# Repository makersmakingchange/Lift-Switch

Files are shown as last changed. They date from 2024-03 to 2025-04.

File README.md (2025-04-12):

<!---  Open Source Assistive Technology: GitHub Readme Template Version 1.1 (2024-Mar-15)  --->

<!-- TITLE --->
# Lift Switch
<!--- SUMMARY -->
<!-- A brief summary of the project. What it does, who it is for, how much it costs. -->
The Lift Switch is a device that modifies the output from your assistive switch. The primary case is for a user who would prefer to rest on their switch and lift off of it to activate it, instead of requiring the user to hover over the switch. There are four operating modes: momentary, latching, timed latch, and reverse acting, described below:
- Momentary: The output will turn on momentarily when you lift off of the assistive switch.
- Latching: The output toggles between on/off when you lift off of the assistive switch.
- Timed Latch: The output will turn on for a set amount of time (7s) when you lift off of the assistive switch.
- Reverse Acting: Reverses the action of an assistive switch. Assistive switch off (not activated) = Lift Switch on, Assistive switch on (activated) = Lift Switch off.

The Lift Switch can also be used as a mouse click in any of the above modes, by plugging the Lift Switch into a computer through a USB cable.

The total cost of materials to build this device is around \$75 (plus component shipping). The cost of materials per unit is around \$43 (plus component shipping) if you are able to build in bulk.

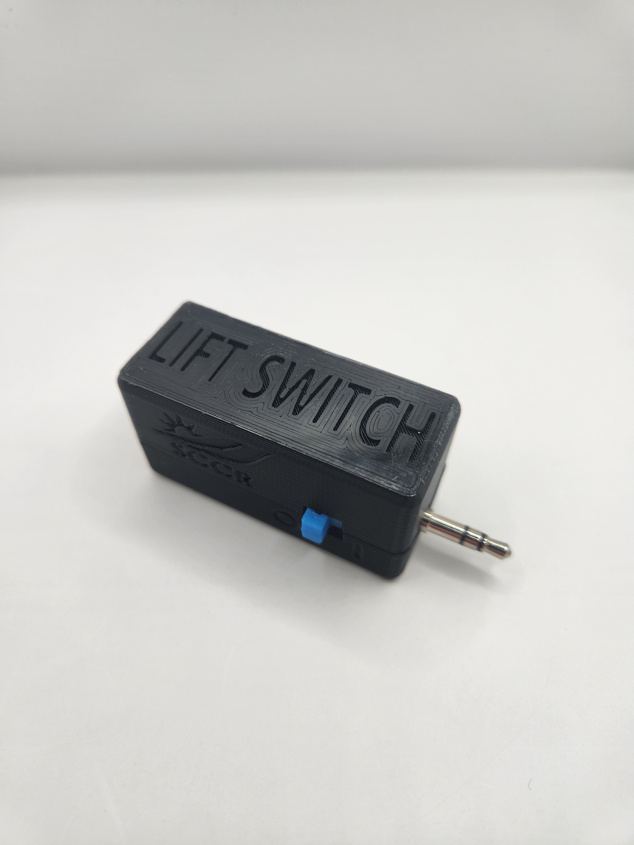
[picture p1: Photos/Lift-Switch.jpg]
Picture of the Lift Switch.


## Makers Making Change Assistive Device Library Listing
- https://www.makersmakingchange.com/s/product/lift-switch/01tJR000003UiczYAC

## How to Obtain the Device
### 1. Do-it-Yourself (DIY) or Do-it-Together (DIT)

This is an open-source assistive technology, so anyone is free to build it. All of the files and instructions required to build the device are contained within this repository. Refer to the Maker Guide below.

### 2. Request a build of this device

You may also submit a build request through the [Makers Making Change Assistive Device Library Listing](https://www.makersmakingchange.com/s/product/lift-switch/01tJR000003UiczYAC) to have a volunteer maker build the device. As the requestor, you are responsible for reimbursing the maker for the cost of materials and any shipping.

### 3. Build this device for someone else

If you have the skills and equipment to build this device, and would like to donate your time to create the device for someone who needs it, visit the [MMC Maker Wanted](https://makersmakingchange.com/maker-wanted/) section.

## Build Instructions

### 1. Read through the Maker Guide

The [Maker Guide](/Documentation/Lift_Switch_Maker_Guide.pdf) contains all the necessary information to build this device, including tool lists, assembly instructions, programming instructions and testing.

### 2. Order the Off-The-Shelf Components

The [Bill of Materials](/Documentation/Lift_Switch_BOM.csv) lists all of the parts and components required to build the device.

### 3. Order the Custom PCB

This device requires a custom PCB. Instructions are provided in the [Maker Guide](/Documentation/Lift_Switch_Maker_Guide.pdf) and the PCB fabrication files are available in the [PCB Build Files](/Build_Files/PCB_Build_Files).

### 4. Print the 3D Printable components

All of the files and individual print files can be in the [/Build_Files/3D_Printing_Files](/Build_Files/3D_Printing_Files/) folder.

### 5. Assemble the Lift Switch

Reference the [Maker Guide](/Documentation/Lift_Switch_Maker_Guide.pdf) for the tools and steps required to build each portion.

## How to improve this Device
As open source assistive technology, you are welcomed and encouraged to improve upon the design. 

## Files
### Documentation
| Document             | Version | Link |
|----------------------|---------|------|
| Maker Guide          | 1.0     | [Lift_Switch_Maker_Guide](/Documentation/Lift_Switch_Maker_Guide.pdf)     |
| Bill of Materials    | 1.0     | [Lift_Switch_Bill_of_Materials](/Documentation/Lift_Switch_BOM.csv)     |
| User Guide           | 1.0     | [Lift_Switch_User_Guide](/Documentation/Lift_Switch_User_Guide.pdf)    |
| Changelog            | 1.0     | [Changelog](CHANGES.txt)     |

### Design Files
<!---
DESIGN FILES
Include a copy of the original design files to facilitate easy editing and customization. Consider also including a generic format (e.g., STEP)
--->
 - [CAD Files](/Design_Files/CAD_Design_Files)
 - [PCB Files](/Design_Files/PCB_Design_Files)

<!---
BUILD FILES
Include a copy of the build files intended for manufacturing. This may include svg files for laser cutting, stl files for 3d printing, Gerber files for custom PCBs, and Arduino files for custom firmware
--->
### Build Files
 - [3D Printing Files](/Build_Files/3D_Printing_Files)
 - [PCB Build Files](/Build_Files/PCB_Build_Files)
 - [Firmware Files](/Build_Files/Firmware_Files)

<!---
ATTRIBUTION
Provide any necessary attribution for designs or components that are included in the device or as part of the project.
--->
## Attribution

The Lift Switch was designed by the Rehabilitation Engineering Department at Horizon Health's Stan Cassidy Centre for Rehabilitation (SCCR). Development was supported through the Government of Canada's Innovation Science and Economic Development  [Accessible Technology Program](https://ised-isde.canada.ca/site/accessible-technology-program). The ATP program enabled SCCR to deploy numerous Lift Switches to users at reduced cost.

The latest design (V2.0) incorporates feedback and suggestions from numerous users, clinicians, and volunteer makers.

The latest design incorporates several commercially available open source hardware components from [Adafruit](https://www.adafruit.com/). The Lift Switch firmware utilizes the [Arduino](https://www.arduino.cc/) development platform, and a number of libraries developed and shared by the open source community.

<!---
This is the attribution for the template.
--->
The documentation template was created by Makers Making Change / Neil Squire Society and is used under a CC BY-SA 4.0 license. It is available at the following link: [https://github.com/makersmakingchange/OpenAT-Template](https://github.com/makersmakingchange/OpenAT-Template)

<!---
CONTRIBUTORS
List the names of the people that contributed to the design. This could include the original source of the idea, designers, testers, documenters, etc.
--->
### Contributors

- Rachelle Bernier, Horizon Health Network.
- Marla Calder, Horizon Health Network
- Natasha Hanson, Horizon Health Network
- Dorian Hawkes, Horizon Health Network
- Rick McCaskill, Horizon Health Network
- Billie O'Connor, Horizon Health Network
- Kristen Culberson, Horizon Health Network
- Josie Versloot, Neil Squire Society / Makers Making Change

<!---
LICENSE
Add the year(s) for the copyright and the Designer Name. You may use the standard set of open licenses or choose your own for the hardware, software, and accompanying materials.
--->
## License
Copyright (c) 2020-2024 Stan Cassidy Centre for Rehabilitation.

This repository describes Open Hardware:
 - Everything needed or used to design, make, test, or prepare the Lift Switch is licensed under the [CERN 2.0 Weakly Reciprocal license (CERN-OHL-W v2) or later](https://cern.ch/cern-ohl ) .
 - All software is under the [GNU General Public License v3.0 (GPL-3.0)](https://www.gnu.org/licenses/gpl.html).
 - Accompanying material such as instruction manuals, videos, and other copyrightable works that are useful but not necessary to design, make, test, or prepare the Lift Switch are published under a [Creative Commons Attribution-ShareAlike 4.0 license (CC BY-SA 4.0)](https://creativecommons.org/licenses/by-sa/4.0/) .

You may redistribute and modify this documentation and make products using it under the terms of the [CERN-OHL-W v2](https://cern.ch/cern-ohl).
This documentation is distributed WITHOUT ANY EXPRESS OR IMPLIED WARRANTY, INCLUDING OF MERCHANTABILITY, SATISFACTORY QUALITY AND FITNESS FOR A PARTICULAR PURPOSE.
Please see the CERN-OHL-W v2 for applicable conditions.

Source Location: https://github.com/makersmakingchange/Lift-Switch

List of open source licenses. Hardware: CERN-OHL-W-2.0, Software: GPL-3.0-or-later, Documentation: CC-BY-SA-4.0.

----

<!-- ABOUT MMC START -->
## About Makers Making Change
[Makers Making Change Logo](https://www.makersmakingchange.com/)

Makers Making Change is a program of [Neil Squire](https://www.neilsquire.ca/), a Canadian non-profit that uses technology, knowledge, and passion to empower people with disabilities.

Makers Making Change leverages the capacity of community based Makers, Disability Professionals and Volunteers to develop and deliver affordable Open Source Assistive Technologies.

 - Website: [www.MakersMakingChange.com](https://www.makersmakingchange.com/)
 - GitHub: [makersmakingchange](https://github.com/makersmakingchange)
 - Bluesky: [@makersmakingchange.bsky.social](https://bsky.app/profile/makersmakingchange.bsky.social)
 - Instagram: [@makersmakingchange](https://www.instagram.com/makersmakingchange)
 - Facebook: [makersmakechange](https://www.facebook.com/makersmakechange)
 - LinkedIn: [Neil Squire Society](https://www.linkedin.com/company/neil-squire-society/)
 - Thingiverse: [makersmakingchange](https://www.thingiverse.com/makersmakingchange/about)
 - Printables: [MakersMakingChange](https://www.printables.com/@MakersMakingChange)

### Contact Us
For technical questions, to get involved, or to share your experience we encourage you to [visit our website](https://www.makersmakingchange.com/) or [contact us](https://www.makersmakingchange.com/s/contact).
<!-- ABOUT MMC END -->

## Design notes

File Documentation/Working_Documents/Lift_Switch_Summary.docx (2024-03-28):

This document is intended to be a summary of a device to make it easier to add to the website.

# Product Information

## Product Name

Lift Switch

## Device Category

| Adapted Toys
| Aids for Daily Living (ADL)
X | Assistive Switches
| Communication Aids (AAC)
X | Computer Access
| Environmental Controls
X | Gaming
| Keyguard
| Kits
| LipSyncs
| Mounting
| Recreation and Leisure
| Seating and Positioning
X | Switch Interfaces
| Writing Aids

## User Value Statement

For assistive switch users who would like to activate their switch by resting on the switch and lifting off, instead of pushing down, the Lift Switch Interface will modify the output of any standard 3.5mm assistive switch!

## Designer

Stan Cassidy Centre for Rehabilitation

# Device Info

## Overview

The Lift Switch is a device that modifies the output from your assistive switch. The primary case is for a user who would prefer to rest on their switch and lift off of it to activate it, instead of requiring the user to hover over the switch. There are four operating modes: momentary, latching, timed latch, and reverse acting, described below:

- Momentary – The output will turn on momentarily when you lift off of the assistive switch.
- Latching – The output toggles between on/off when you lift off of the assistive switch.
- Timed Latch – The output will turn on for a set amount of time (7s) when you lift off of the assistive switch.
- Reverse Acting - Reverses the action of an assistive switch. Assistive switch off (not activated) = Lift Switch on, Assistive switch on (activated) = Lift Switch off.

The Lift Switch can also be used as a mouse click in any of the above modes, by plugging the Lift Switch into a computer through a USB cable.

## Disability Type

Select one or more disability types:

X | Agility / Dexterity
| Arthritis
| Cognitive
| Hearing
| Mobility
X | Mobility
X | Other
X | Pain
X | SCI
| Vision

## Disability Type Description

The Lift Switch is designed primarily for disabilities that affect a user’s strength and endurance. The Lift Switch also enables use of switch sites where a user has movement but would otherwise choose not to use it due to ergonomic considerations, for example an accessible switch under an elbow when resting on an armrest. The Lift Switch has been used by people with various disabilities and diagnoses such as ALS, Muscular Dystrophy and MS.

## How To Use

To use the Lift Switch, simply plug in an assistive switch into the 3.5 mm jack, and plug the other end of the lift switch into your switch adapted device.

To change operating modes, press the Mode button located on the side of the Lift Switch. The selected mode is indicated by the light colour, as described below:

- Green - Momentary – The output will turn on momentarily when you lift off of the assistive switch.
- Blue - Latching – The output toggles between on/off when you lift off of the assistive switch.
- Yellow - Timed Latch – The output will turn on for a set amount of time (7s) when you lift off of the assistive switch.
- Red - Reverse Acting - Reverses the action of an assistive switch. Assistive switch off (not activated) = Lift Switch on, Assistive switch on (activated) = Lift Switch off.

To use the Lift Switch as a mouse click, simply plug it into your computer, tablet, or smart phone, using the correct cable or adapter, and put it into the mode that would work best for you.

## Estimated Cost

The estimated material cost of the device:

| $0 - $10
| $11 - $25
| $26 - $50
X | $51 - $100
| $101 - $250
| $250+

## Attribution

The Lift Switch was designed by the Rehabilitation Engineering Department at Horizon Health’s Stan Cassidy Centre for Rehabilitation (SCCR). Development was supported through the Government of Canada’s Innovation Science and Economic Development Accessible Technology Program (https://can01.safelinks.protection.outlook.com/?reserved=0) (ATP). The ATP program enabled SCCR to deploy numerous Lift Switches to users at reduced cost.

The latest design incorporates feedback and suggestions from numerous users, clinicians, and volunteer makers.

The latest design incorporates several commercially available open source hardware components from Adafruit (https://can01.safelinks.protection.outlook.com/?url=https%3A%2F%2Fwww.adafruit.com%2F&reserved=0). The Lift Switch firmware utilizes the Arduino (https://can01.safelinks.protection.outlook.com/?url=https%3A%2F%2Fwww.arduino.cc%2F&reserved=0) development platform, and a number of libraries developed and shared by the open source community. Full details are available on GitHub (https://can01.safelinks.protection.outlook.com/?reserved=0).

Contributors to this iteration of the Lift Switch:

- Rachelle Bernier, Horizon Health Network.
- Marla Calder, Horizon Health Network
- Natasha Hanson, Horizon Health Network
- Dorian Hawkes, Horizon Health Network
- Rick McCaskill, Horizon Health Network
- Billie O’Connor, Horizon Health Network
- Kristen Culberson, Horizon Health Network
- Josie Versloot, Neil Squire Society / Makers Making Change

# Maker Info

## Project Skills

X | 3D Printing
X | Custom PCB
X | Electronics
| Laser Cutting
| Mechanics
X | Other
X | Software
X | Soldering
| Woodworking

## Skills Description

## This build involves an intermediate level of 3D printing, soldering, Arduino firmware, and assembly. It also involves ordering a custom PCB. This build has some surface mount soldering.

## Tools Needed

X | 3D Printer
X | Common Hand Tools
| Common Power Tools
| Laser Cutter
X | Soldering Iron
| Specialized Tooling

## Print time (hrs)

2.0 hours

## Assembly time (hrs)

1.0 hours

## Build Instructions

The Lift Switch hardware consists of off-the-shelf electronics and hardware components, 3D printed components, and a custom printed circuit board (PCB). The build consist of soldering the parts to the PCB, flashing Arduino code to the microcontroller, and assembling the enclosure. For more detailed build instructions, see the Maker Guide.

## Download Link

## https://github.com/makersmakingchange/Lift-Switch/archive/refs/heads/main.zip

## Project Link

## https://github.com/makersmakingchange/Lift-Switch

# License

## License

Copyright (c) 2024 Stan Cassidy Centre for Rehabilitation.

This repository describes Open Hardware:

- Everything needed or used to design, make, test, or prepare the Lift Switch is licensed under the CERN 2.0 Weakly Reciprocal license (CERN-OHL-W v2) or later (https://cern.ch/cern-ohl) .
- All software is under the GNU General Public License v3.0 (GPL-3.0) (https://www.gnu.org/licenses/gpl.html).
- Accompanying material such as instruction manuals, videos, and other copyrightable works that are useful but not necessary to design, make, test, or prepare the Lift Switch are published under a Creative Commons Attribution-ShareAlike 4.0 license (CC BY-SA 4.0) (https://creativecommons.org/licenses/by-sa/4.0/) .

You may redistribute and modify this documentation and make products using it under the terms of the CERN-OHL-W v2 (https://cern.ch/cern-ohl). This documentation is distributed WITHOUT ANY EXPRESS OR IMPLIED WARRANTY, INCLUDING OF MERCHANTABILITY, SATISFACTORY QUALITY AND FITNESS FOR A PARTICULAR PURPOSE. Please see the CERN-OHL-W v2 for applicable conditions.

Source Location: https://github.com/makersmakingchange/Lift-Switch

© 2024 by Stan Cassidy Centre for Rehabilitation This work is licensed under the CC BY SA 4.0 License: http://creativecommons.org/licenses/by-sa/4.0 Page 1 of 2

V2.0 | MARCH 2024 Lift Switch Summary

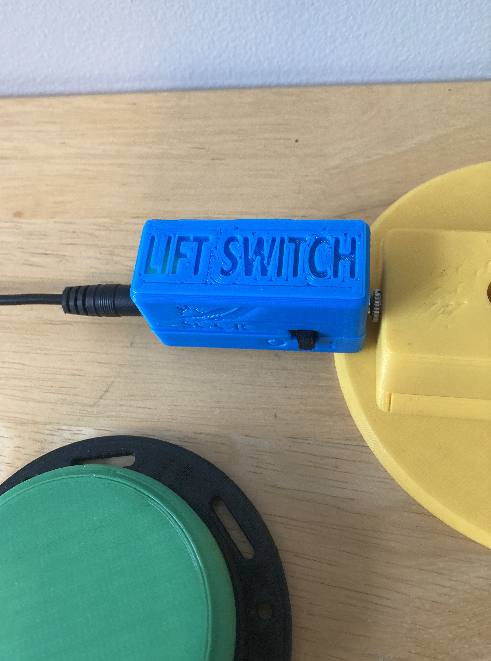
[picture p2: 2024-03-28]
Photos/Lift-Switch-Toy-Closeup.jpg

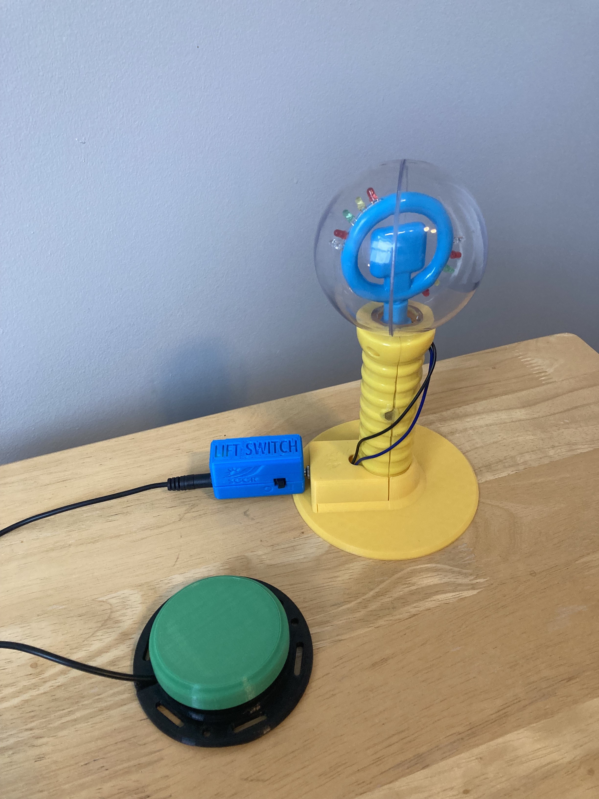
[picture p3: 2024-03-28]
Photos/Lift-Switch-Toy2.jpg

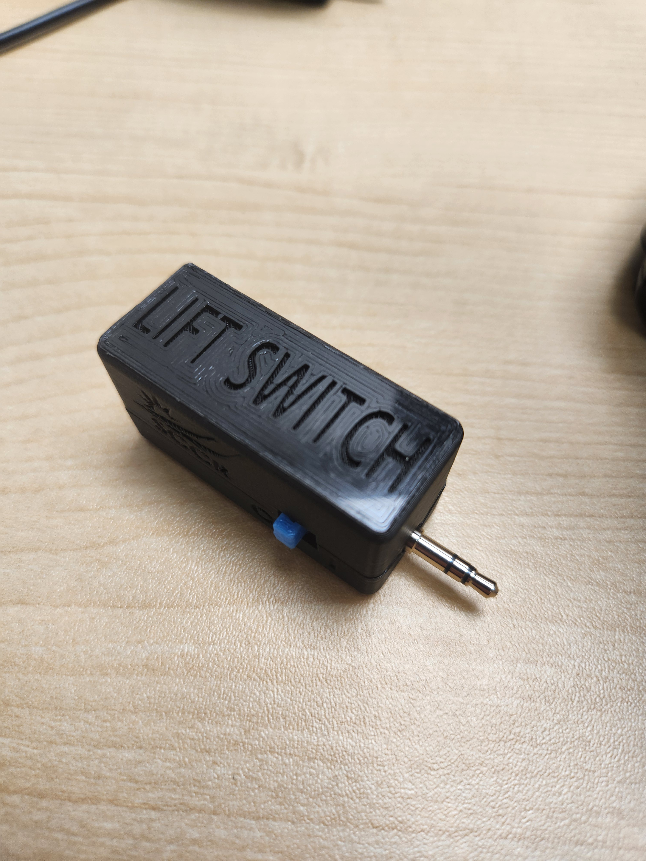
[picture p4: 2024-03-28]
Photos/Lift-Switch2.jpg

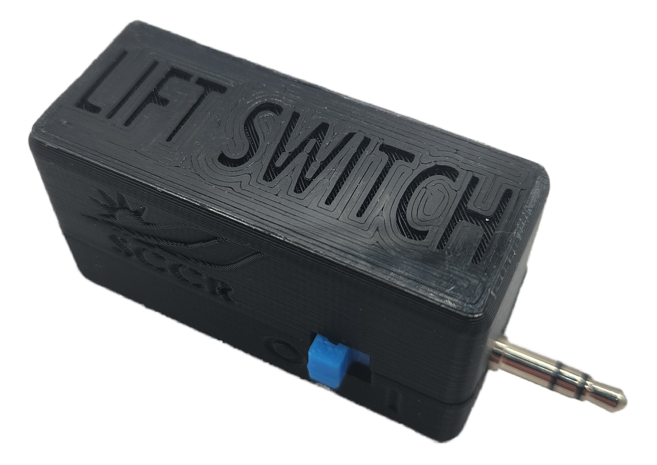
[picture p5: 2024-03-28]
Photos/Lift-Switch_NoBackground.png

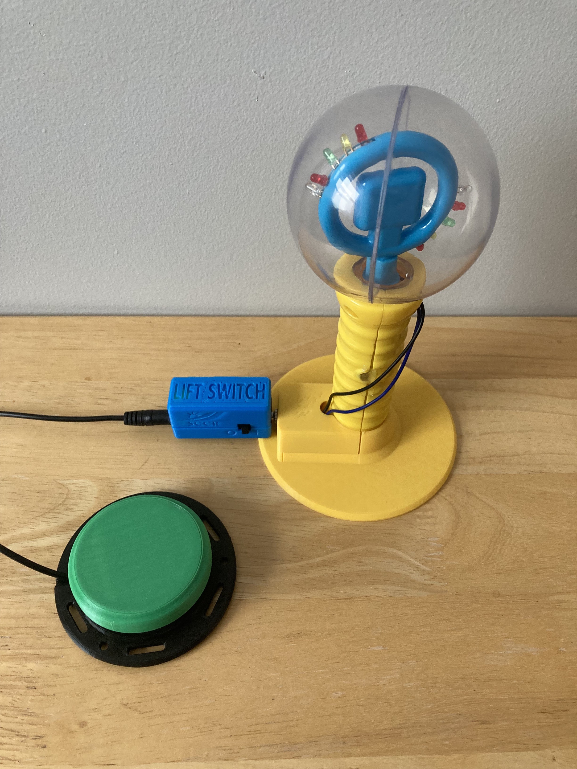
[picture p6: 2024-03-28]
Photos/Lift-Switch-Toy.jpg

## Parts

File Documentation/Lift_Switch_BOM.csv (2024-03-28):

 | Lift Switch |  |  |  |  |  |  |  | Total filament (g) |  |  | Unit Cost | Total Cost | Total Print time (hr)
 | Version: | 2.0 |  | Last updated: | 2024-Mar-25 |  |  |  | 15 |  |  | $42.99 | $77.57 | 1:51
ID | Part | Description |  | Manufacturer | MPN | Supplier | Supplier PN | QTY | QTY / PKG | PKGs | $/PKG | Price per Unit | Total Price |  | Link | Alternate
 | Electronics
C | XA2 | PRO TRINKET LI-BATTERY BACKPACK |  | Adafruit Industries LLC | 2124 | Digi-Key | 1528-1443-ND | 1 | 1 | 1 | 7.29 | $7.29 | $7.29 |  | https://www.digikey.ca/en/products/detail/adafruit-industries-llc/2124/5761211
B | XA1 | TRINKET M0 ATSAMD21E18 EVAL BRD |  | Adafruit Industries LLC | 3500 | Digi-Key | 1528-2361-ND | 1 | 1 | 1 | 13.17 | $13.17 | $13.17 |  | https://www.digikey.ca/en/products/detail/adafruit-industries-llc/3500/7623049
D | J1 | CONN JACK STEREO 3.5MM TH R/A |  | Kycon, Inc. | STX-3000 | Digi-Key | 2092-STX-3000-ND | 1 | 1 | 1 | 1.18 | $1.18 | $1.18 |  | https://www.digikey.ca/en/products/detail/kycon-inc/STX-3000/9975995
H | SW1 | SWITCH SLIDE SPDT 100MA 12V |  | Nidec Copal Electronics | CSS-1210TB | Digi-Key | 563-1091-1-ND | 1 | 1 | 1 | 0.91 | $0.91 | $0.91 |  | https://www.digikey.ca/en/products/detail/nidec-components-corporation/CSS-1210TB/1124209
E | U1 | DIP-4 400V/120 MA, SSR RELAY SPS |  | Bright Toward Industrial Co., Ltd. | AB30 | Digi-Key | 3008-AB30-ND | 1 | 1 | 1 | 2.72 | $2.72 | $2.72 |  | https://www.digikey.ca/en/products/detail/bright-toward-industrial-co-ltd/AB30/13556959
G | SW2 | 6 X 7.4 MM, 15.3 MM ACTUATOR HEI |  | CUI Devices | TS11-674-153-BK-260-RA-D | Digi-Key | 2223-TS11-674-153-BK-260-RA-D-ND | 1 | 1 | 1 | 0.24 | $0.24 | $0.24 |  | https://www.digikey.ca/en/products/detail/cui-devices/TS11-674-153-BK-260-RA-D/16562823
F | R1 | RES 330 OHM 5% 1/4W AXIAL |  | YAGEO | CFR-25JB-52-330R | Digi-Key | 330QBK-ND | 1 | 1 | 1 | 0.16 | $0.16 | $0.16 |  | https://www.digikey.ca/en/products/detail/yageo/CFR-25JB-52-330R/1636
I |  | 3.5 mm digital output plug |  | CUI Devices | SP-3533-02 | Digi-Key | 102-4747-ND | 1 | 1 | 1 | 2.68 | $2.68 | $2.68 |  | https://www.digikey.ca/en/products/detail/cui-devices/SP-3533-02/9486641
M |  | LIGHT PIPE RA. 150 3MM ROUND |  | Bivar Inc | SLP3-150-450-R | Digikey | 492-2519-ND | 1 | 1 | 1 | 1.19 | $1.19 | $1.19 |  | https://www.digikey.ca/en/products/detail/bivar-inc/SLP3-150-450-R/4926816
N |  | 3.7V 110 mAh lithium-ion polymer battery |  | Canada Robotix | 0930 | Canada Robotix |  | 1 | 1 | 1 | 5.99 | $5.99 | $5.99 |  | https://www.canadarobotix.com/products/939
Q |  | M2x0.4 x 25 mm screws, flat head |  | McMaster Carr | 92010A111 | McMaster Carr | 92010A111 | 3 | 50 | 1 | $9.31 | $0.56 | $9.31 |  | https://www.mcmaster.com/catalog/130/3484/92010A111
 |  |  |  |  |  |  |  |  |  | 0 |  | $- | $-
 | Custom PCB
 | Part | Description |  | Manufacturer |  | Supplier | Supplier PN | QTY | QTY / PKG | PKG | $/PKG | Price per Unit | Total Price |  | Link
A | PCB1 | Lift Switch Adapter Custom PCB |  | JLCPCB |  |  |  | 1 | 5 | 1 | 7.28 | 1.46 | 7.28
 | PCB Shipping | PCB Shipping - DHL Express | Shipping |  |  |  |  | 1 | 5 | 1 | 25 | 5 | 25
 | PCB Shipping | PCB Shipping - Fedex International | Shipping |  |  |  |  | 0 | 5 | 0 | 25 | 0 | 0
 | 3D Printed Parts ESTIMATED PRICING USING 1KG ROLL COST: | $30.00
 | Part | Description |  |  |  |  |  | QTY | Mass (g) |  | Estimated Price | Estimated Price | Estimated Price | Print Time (hr:Min) | Link
O.1 |  | Lift Switch Base |  |  |  |  |  | 1 | 6 |  | $0.18 | $0.18 | $0.18 | 0:41
O.2 |  | Lift Switch Top |  |  |  |  |  | 1 | 8 |  | $0.24 | $0.24 | $0.24 | 1:07
P |  | Lift Switch Power Switch |  |  |  |  |  | 1 | 1 |  | $0.03 | $0.03 | $0.03 | 0:03
 |  |  |  |  |  |  |  |  |  |  | $- | $- | $-
 | Alternatives
 | Part | Description |  | Manufacturer |  | Supplier
 |  |  |  |  |  |  |  |  | 1 | 0 |  | $- | $-
 |  |  |  |  |  |  |  |  | 1 | 1 |  | $- | $-
 |  |  |  |  |  |  |  |  | 1 | 1 |  | $- | $-

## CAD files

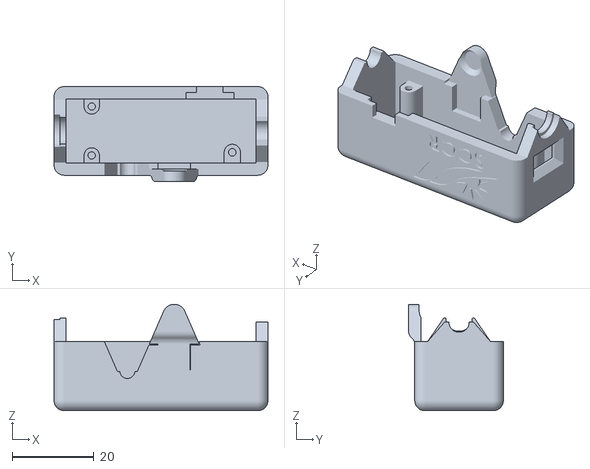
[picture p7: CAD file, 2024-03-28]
Build_Files/3D_Printing_Files/Lift_Switch_Top_v2.STL
52.5 x 23.2 x 26.1

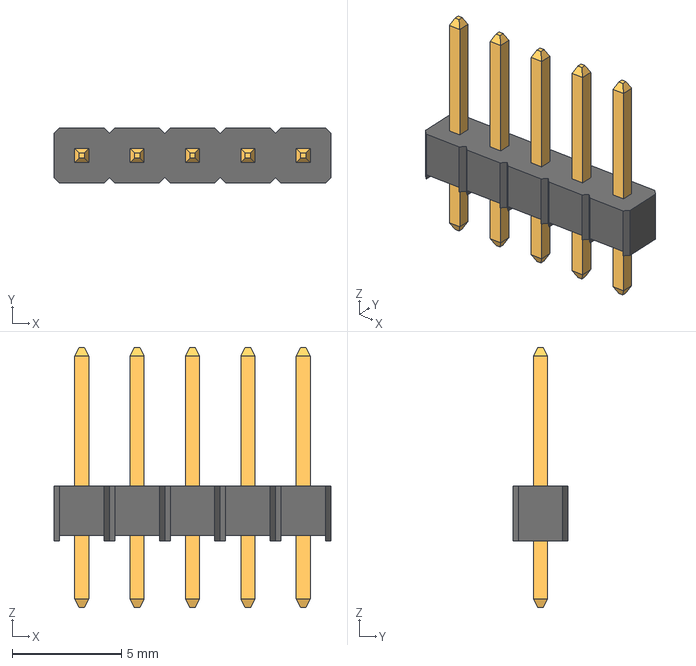
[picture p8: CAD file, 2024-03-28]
Design_Files/PCB_Design_Files/Lift Switch KiCad/3d models/5-Pin Header - Male - 2.54mm.step
12.7 x 2.54 x 11.9 mm

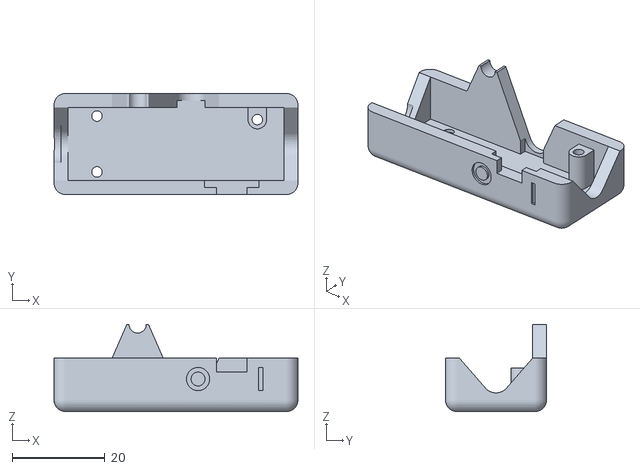
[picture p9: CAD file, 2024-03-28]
Build_Files/3D_Printing_Files/Lift_Switch_Base_v2.STL
52.5 x 21.8 x 18.8

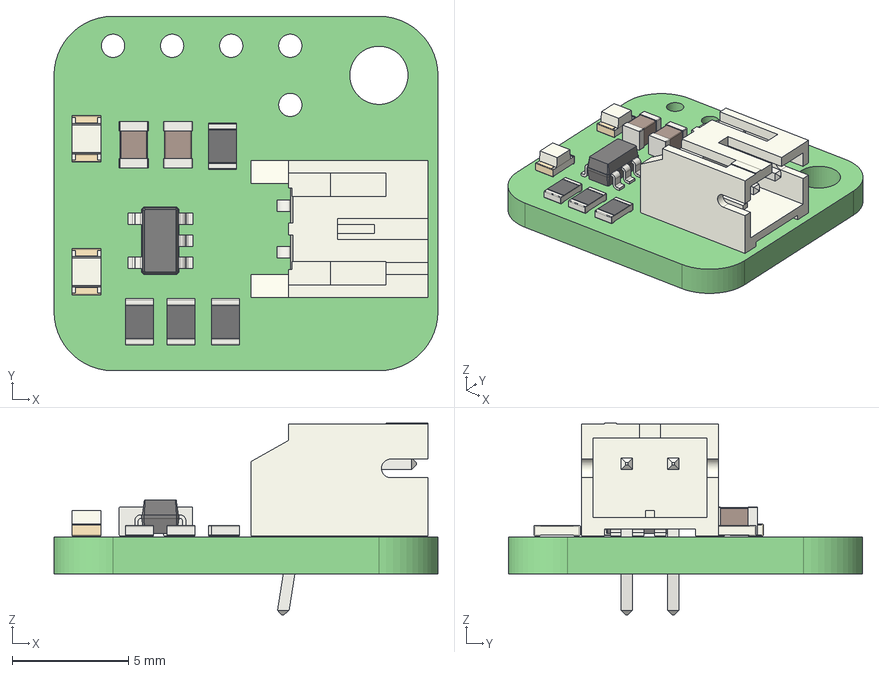
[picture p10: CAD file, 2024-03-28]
Design_Files/PCB_Design_Files/Lift Switch KiCad/3d models/Adafruit protrinket backpack.step
16.5 x 15.2 x 8.25 mm
Adafruit protrinket backpack PCB

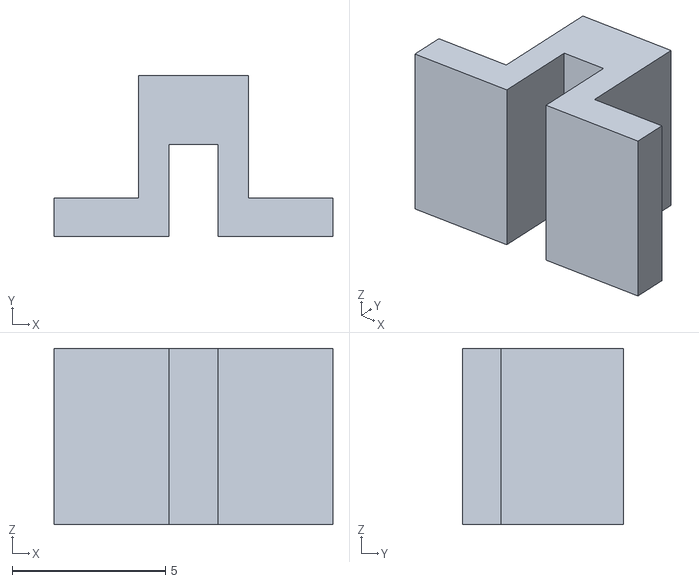
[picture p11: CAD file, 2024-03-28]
Build_Files/3D_Printing_Files/Lift_Switch_Power_Switch_v2.STL
9.10 x 5.25 x 5.75

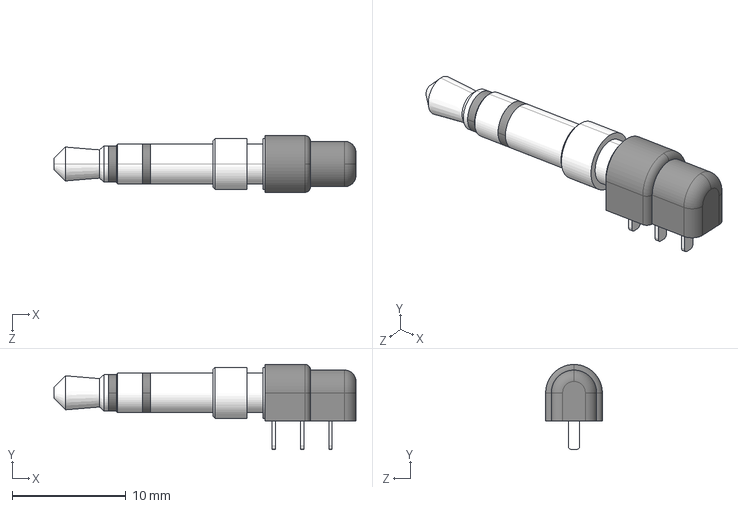
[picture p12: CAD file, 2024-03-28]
Design_Files/PCB_Design_Files/Lift Switch KiCad/3d models/CUI_DEVICES_SP-3533-02.step
26.6 x 7.50 x 5.00 mm

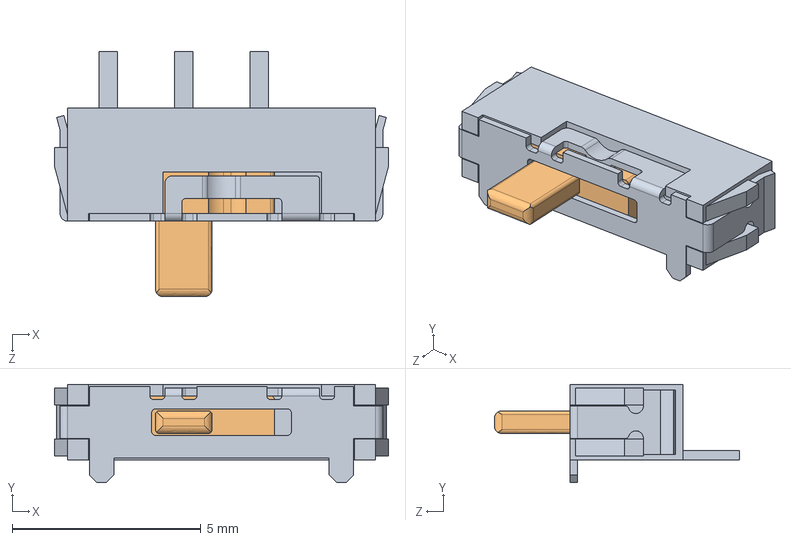
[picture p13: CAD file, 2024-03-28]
Design_Files/PCB_Design_Files/Lift Switch KiCad/3d models/CSS-1210TB.STEP
8.85 x 2.60 x 6.50 mm

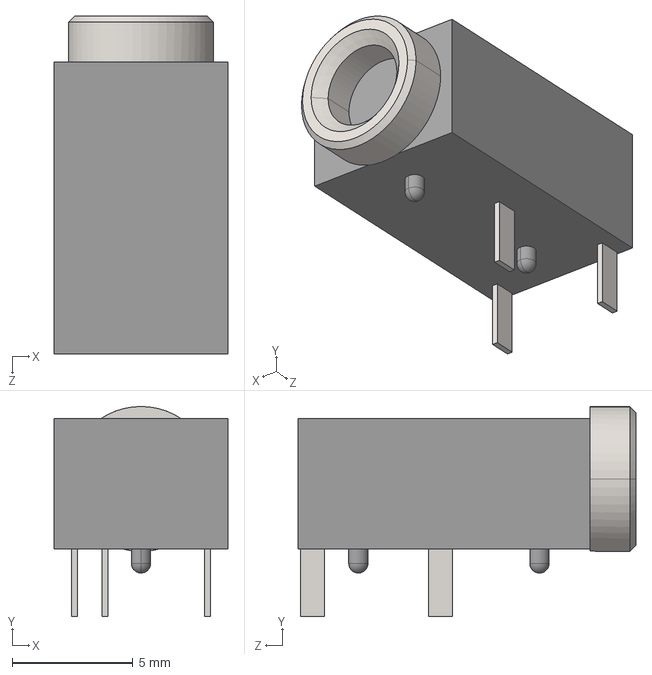
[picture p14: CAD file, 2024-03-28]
Design_Files/PCB_Design_Files/Lift Switch KiCad/3d models/STX-3000.STEP
7.20 x 8.70 x 14.0 mm

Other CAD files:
Design_Files/CAD_Design_Files/Step/Lift_Switch_Top_v2.STEP
Design_Files/CAD_Design_Files/Step/Lift_Switch_Base_v2.STEP
Design_Files/CAD_Design_Files/Step/Lift_Switch_Power_Switch_v2.STEP
Design_Files/CAD_Design_Files/SolidWorks/LiftSwitch_Base_v2.SLDPRT
Design_Files/CAD_Design_Files/SolidWorks/Lift_Switch_Power_Switch_v2.SLDPRT
Design_Files/CAD_Design_Files/SolidWorks/Lift_Switch_Top_v2.SLDPRT

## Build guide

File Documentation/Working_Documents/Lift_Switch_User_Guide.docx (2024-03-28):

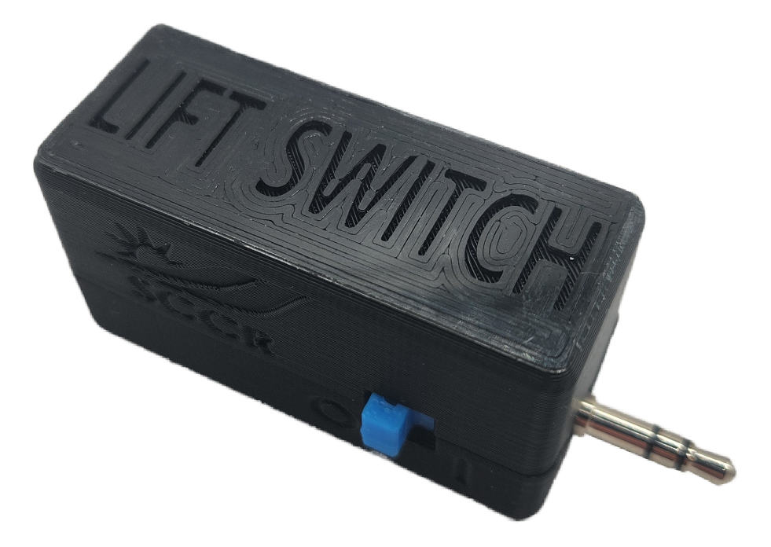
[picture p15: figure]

# Lift Switch User Guide

V2.0 – March 2024

# Disclaimer/Assumption of Risk

The Lift Switch device is not to be used in life support or life safety applications. Such use is entirely at the User’s risk, and the User agrees to defend, indemnify, and hold harmless the Stan Cassidy Center for Rehabilitation from any and all damages, claims, suits, or expenses resulting from such use.

# Introduction

The Lift Switch is an accessibility device that enables specific switch output functions. For example, the user may rest a hand or foot on an adaptive switch, such as a Buddy Button™. Your adapted device is then activated by lifting off the adaptive switch, hence the name “Lift Switch”.

The Lift Switch has 4 modes of operation that can offer a variety of solutions to switch-adapted devices. These modes will be described in more detail below.

# Features

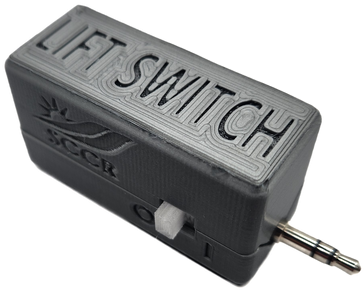
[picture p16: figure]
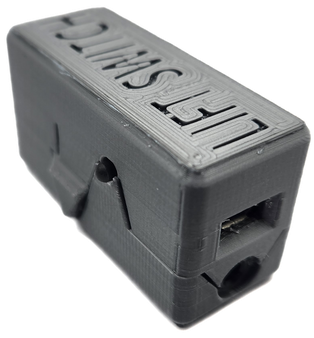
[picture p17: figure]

Output Plug

Power Switch

Mode Button

Indicator Light

Micro-USB Port

Assistive Switch Port

# Usage

## Setup

Step 1: Begin by inserting your adaptive switch’s connector into the assistive switch input (the 1/8” jack) located on the end of the Lift Switch.

Some examples of assistive switches are pictured below:

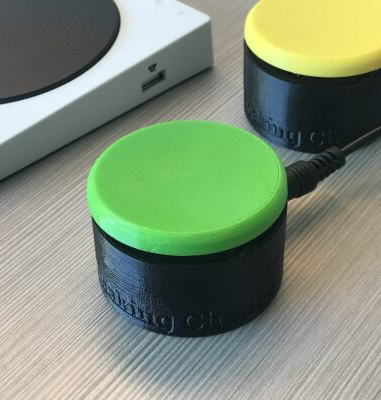
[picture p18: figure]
Picture of two MMC60 switches. One has a green top and one has a yellow top. They are pictured next to a Microsoft Xbox Adaptive Controller.. Click to expand image
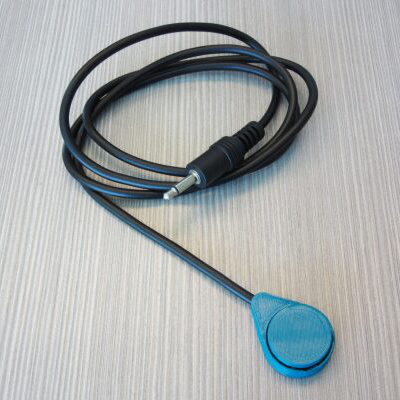
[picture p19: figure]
Raindrop switch. Click to expand image
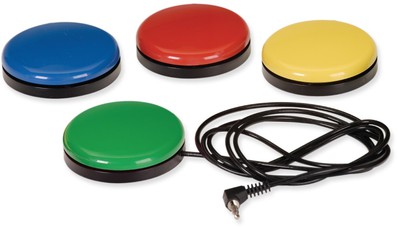
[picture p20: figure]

Step 2: Next, insert the output plug into the adapted device to be controlled, such as an adapted doorbell, light switch or toy.

In this guide, the adapted device will be represented by the Switch Tester (shown below). The red light on the front of the Switch Tester indicates when the device is activated.

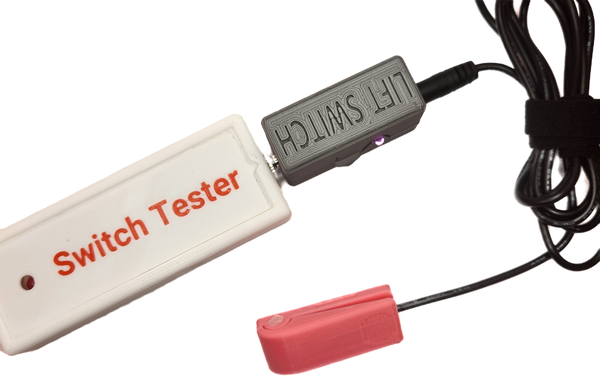
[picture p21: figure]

Step 3: Turn on the Lift Switch by sliding the power switch located on the side into the ON position. The light located on the other side of the Lift Switch module will flash purple intermittently, then will flash green, red, or blue once to indicate the mode the device is in (see page 10 for modes).

If the light does not blink at all, this indicates a low battery. The device will need to be charged before use; see page 9 for charging instructions.

Step 4: Initialize the Lift Switch by pressing and releasing your adaptive switch once.

## Charging Instructions

To charge your device, plug the micro-USB cable into your USB wall adapter or other USB outlet such as on your desktop or laptop, then connect the other end to the micro-USB port of your Lift Switch.

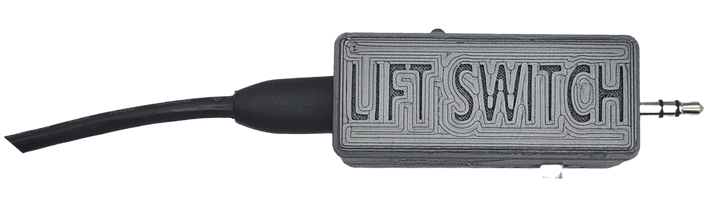
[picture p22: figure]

## Operating Modes

The Lift Switch has 4 modes: Momentary, Latching, Timed Latch, and Reverse Acting. To change modes, press the Mode button located on the side of the Lift Switch (refer to Figure 2). The selected mode is indicated by the light colour, as described in the following table:

Operating Mode | Mode Indicator Light Colour | Mode Overview
Momentary | Green | Lift Switch output will turn on momentarily when you lift off of the assistive switch.
Latching | Blue | Lift Switch output toggles between on/off when you lift off of the assistive switch.
Timed Latch | Yellow | Lift Switch output will turn on for a set amount of time (7s) when you lift off of the assistive switch.
Reverse Acting | Red | Reverses the action of an assistive switch. Assistive switch off (not activated) = Lift Switch on, Assistive switch on (activated) = Lift Switch off.

Please ensure you have completed the setup guide, and that your device is on and charged before trying the different modes. The device will power up in the last mode used.

### Momentary Mode

Step 1: Press the Mode button on the Lift Switch repeatedly until the light is green.

Step 2: Rest on your assistive switch. Your Lift Switch will turn OFF.

Step 3: Lift off of your assistive switch. Your Lift Switch will turn ON for half of a second, activating your adapted device.

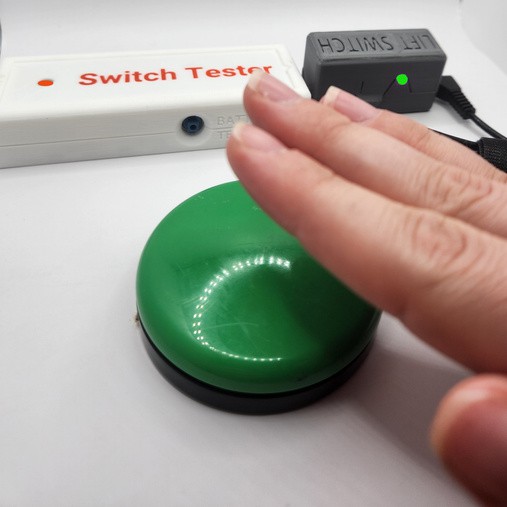
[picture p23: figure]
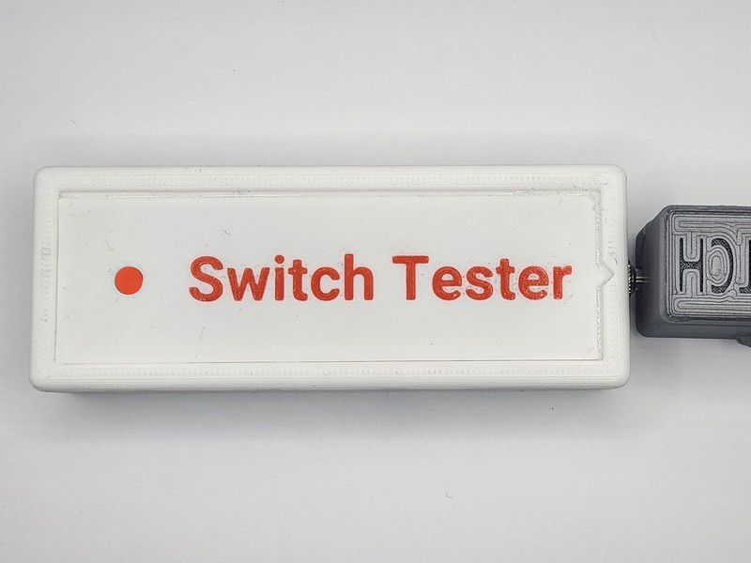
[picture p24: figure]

Step 4: Return to resting on your adaptive switch.

Step 5: Repeat steps 2-4 as necessary.

Note that Lift Switch will activate for half of a second only regardless of how long you remain lifted off of your assistive switch.

### Latching Mode

Step 1: Press the Mode button on the Lift Switch repeatedly until the light is blue.

Step 2: Rest on your adaptive switch. Your Lift Switch will turn OFF.

Step 3: Lift off your adaptive switch. Your Lift Switch will turn ON, activating your adapted device.

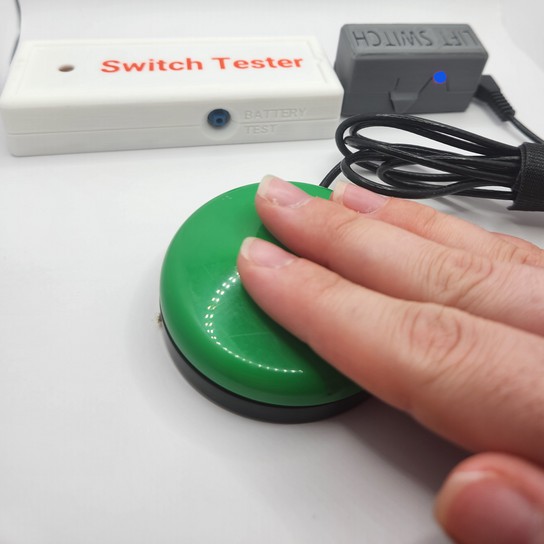
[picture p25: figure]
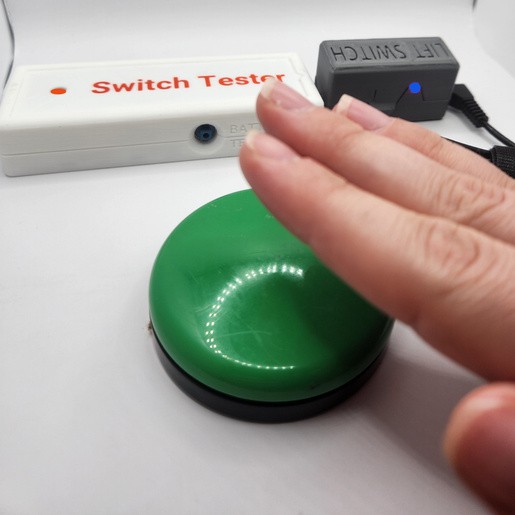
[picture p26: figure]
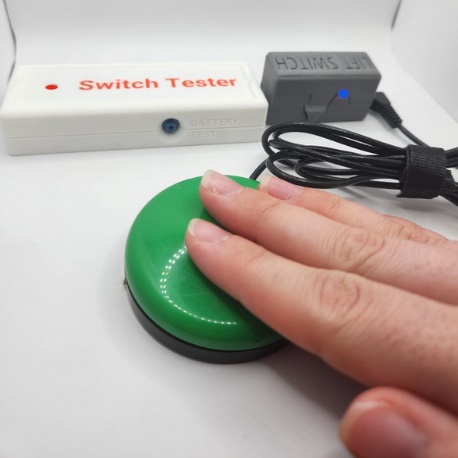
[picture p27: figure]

Step 4: Return to resting on your adaptive switch. Note that your adapted device will stay on.

Step 5: Lift off your adaptive switch again. Your Lift Switch will turn OFF, deactivating your adapted device.

Step 6: Return to resting on your adaptive switch. Note that your adapted device will stay off.

Step 7: Repeat steps 2-6 as necessary.

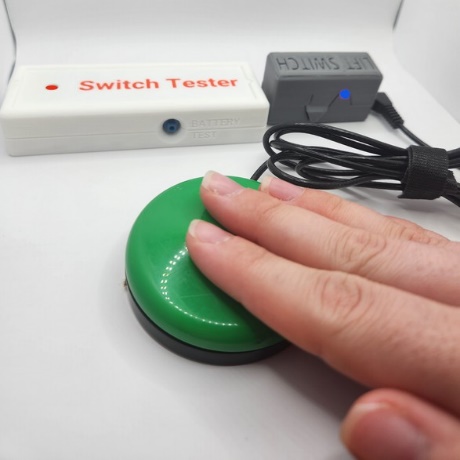
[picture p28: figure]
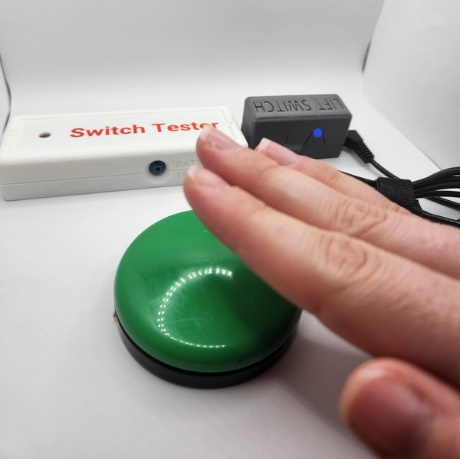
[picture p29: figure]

### Timed Latch Mode

Step 1: Press the Mode button on the Lift Switch repeatedly until the light is yellow.

Step 2: Rest on your adaptive switch. Your Lift Switch will turn OFF.

Step 3: Lift off of your adaptive switch. Your Lift Switch will turn ON for seven seconds, activating your adapted device. Your Lift Switch will turn OFF automatically after seven seconds, deactivating your adapted device.

Step 4: Return to resting on your adaptive switch.

Step 5: Repeat steps 2-4 as necessary.

### Reverse Acting Mode

Step 1: Press the Mode button on the Lift Switch repeatedly until the light is red.

Step 2: Rest on your adaptive switch. Your Lift Switch will turn OFF.

Step 3: Lift off of your adaptive switch. Your Lift Switch will turn ON, activating your adaptive device.

Step 4: Return to resting on your adaptive switch. Your Lift Switch will turn OFF again.

Step 5: Repeat steps 2-4 as necessary.

Notice your Lift Switch will turn on and stay on for the amount of time that you are lifted off your adaptive switch.

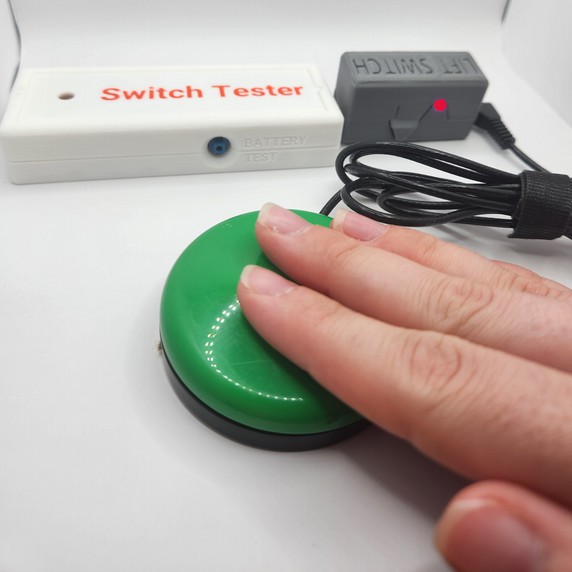
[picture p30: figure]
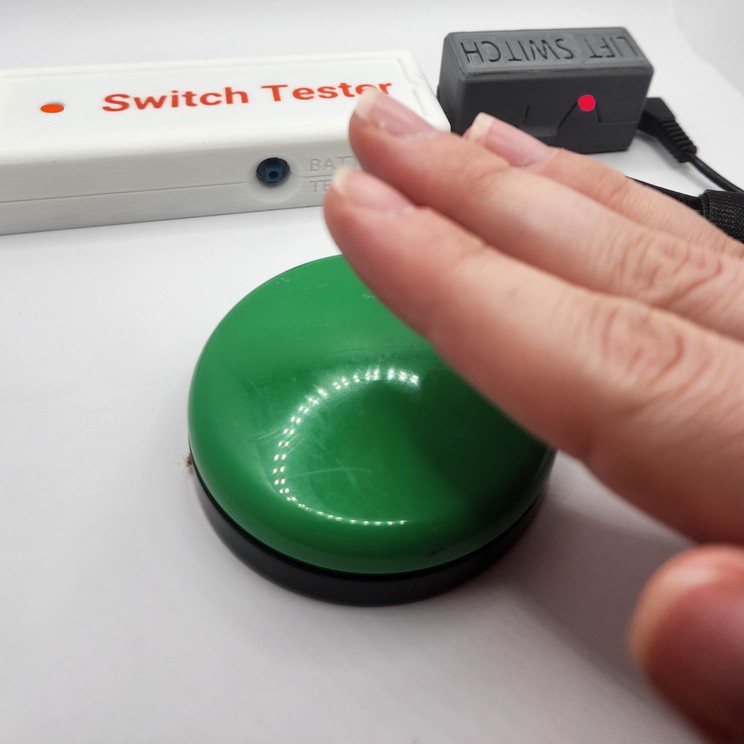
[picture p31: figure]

The adapted device will remain OFF when resting on the adaptive switch.

The adapted device will remain ON when lifted off of the adaptive switch.

## Using the Lift Switch with a Computer or Tablet

You may use your Lift Switch as a mouse-click on your electronic devices. To use the Lift Switch with a computer, simply plug a micro-USB cable into a USB port of your computer and connect the other end to the micro-USB port of your Lift Switch. Note that the output plug is not used with a computer.

If you are using the Lift Switch on a tablet device, you may need to provide your own USB adapter for your specific tablet.

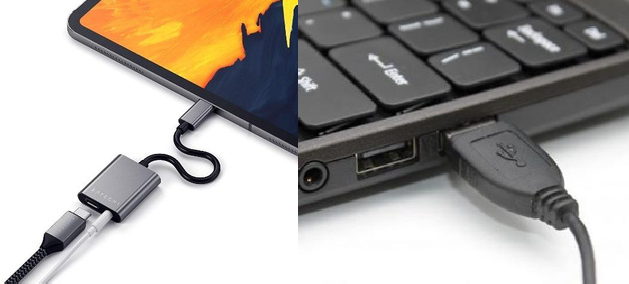
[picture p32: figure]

If using an Apple™ product, you will need to connect your micro-USB cord to the appropriate USB adapter for the Lift Switch to function properly as a mouse click device. Some potential adapters are pictured below:

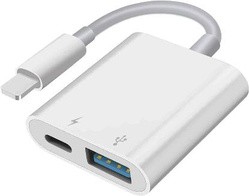
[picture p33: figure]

If you are using an Apple™ device, refer to the online instructions found here: https://support.apple.com/en-us/HT211008 for mouse functions, and
https://support.apple.com/en-ca/HT201370 for Switch Control functions.

This function pairs nicely with switch scanning software or a head mouse device that you would need to acquire on your own.

Below are photos of an iPad set up for accessible use with the Lift Switch using adaptors (left) and a switch-adapted mouse (right):

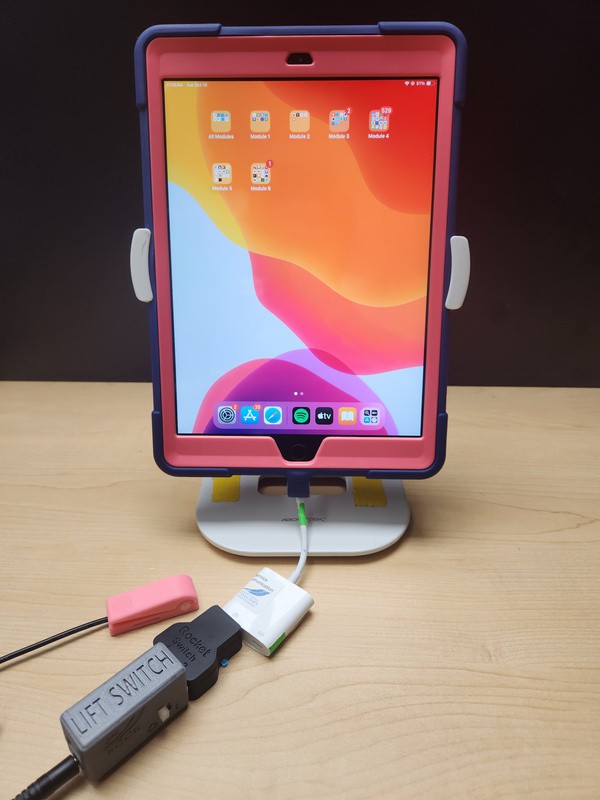
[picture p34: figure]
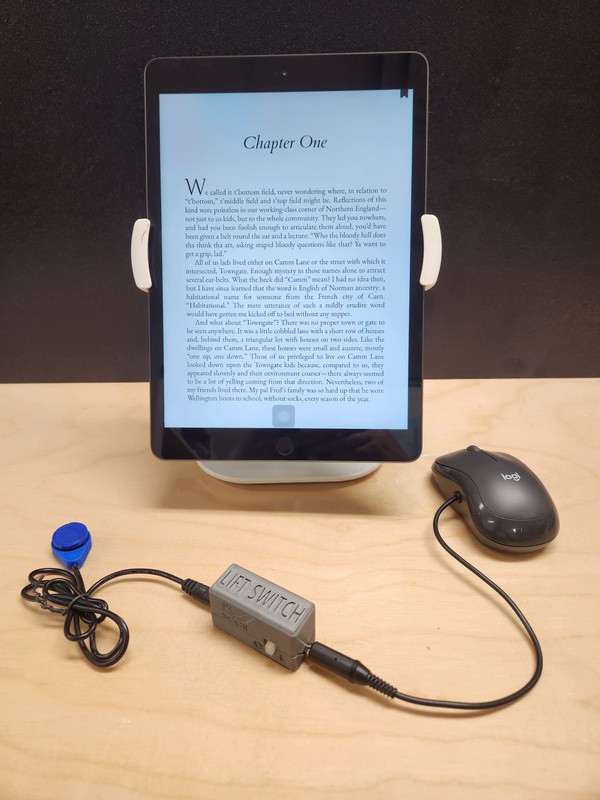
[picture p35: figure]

# Compatibility

The Twitch Switch is compatible with Windows and Mac computers, and both Apple and Android mobile devices.

# Troubleshooting

Problem | Possible Cause | Solution
Won’t turn on; no response when using adapted device | Battery is dead | Charge device
| Device is defective | Contact Makers Making Change
Mouse click is not working on tablet/computer | Connection is bad; cable(s) are defective | Inspect connections and condition of cables; try different cables
| Device is not installed | Under Settings, locate the Lift Switch and allow installation
| Tablet not configured for mouse operation | Configure tablet for mouse input

# Cleaning and Maintenance

To clean your Lift Switch, wipe with a damp cloth or disinfecting wipe.

The Lift Switch is NOT WATERPROOF – DO NOT IMMERSE IN WATER. This would cause permanent damage to the device.

Ensure device is powered OFF after each use to maintain battery life. Charge device between uses of over one hour.

# Specifications

Dimension | Value
Mass | 31 g
Height | 2.9 cm
Length (without plug) | 5.3 cm
Length (with plug) | 6.8 cm
Width | 2.2 cm

© 2024 by Stan Cassidy Research Centre This work is licensed under the CC BY SA 4.0 License: http://creativecommons.org/licenses/by-sa/4.0 Files available at https://github.com/makersmakingchange/Lift-Switch Page 2 of 3

V2.0 | MARCH 2024 Lift Switch Modifier user Guide

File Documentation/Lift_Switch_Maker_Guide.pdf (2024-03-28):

V2.0 | MARCH 2024

## Lift Switch

## MAKER GUIDE

© 2024 by Stan Cassidy Centre for Rehabilitation This work is licensed under the CC BY SA 4.0 License: http://creativecommons.org/licenses/by-sa/4.0
Files available at https://github.com/makersmakingchange/Lift-Switch | Page 1 of 22

### Overview

This document contains the necessary information to build the device.

### Contents

## MAKER GUIDE

Files available at https://github.com/makersmakingchange/Lift-Switch | Page 2 of 22

## MAKER GUIDE

Files available at https://github.com/makersmakingchange/Lift-Switch | Page 3 of 22

### Maker Checklist

This list provides an overview of the steps required to build and deliver the device.

### Maker To Do List

Read through the Assembly Guide to become familiar with required components, tools, supplies, and safety gear and overall assembly steps.
Ask user if they have or need an assistive switch.
Ask user if they have or need a switch accessible device (adapted toy, adapted mouse, switch interface, etc.).
Talk to user about customization options (e.g., color, any special requests, etc.).
Order hardware components.
Gather tools, supplies, and safety equipment.
Assemble the device.
Test device.
Print User Guide.

### Items to Give to User

Assembled, tested device.
User Guide.
Micro-USB cable.

## MAKER GUIDE

Files available at https://github.com/makersmakingchange/Lift-Switch | Page 4 of 22

### Tool List

- Fine-tipped soldering iron
- Solder
- Flush Cutters
- Utility Knife
- Breadboard or small clamp
- Electrical tape
- Multimeter
- Micro-USB cable
- Accessible switch and switch tester (for testing)

## MAKER GUIDE

Files available at https://github.com/makersmakingchange/Lift-Switch | Page 5 of 22

### Custom PCB Guide

The Lift Switch uses one custom circuit board.

The Custom PCB can be ordered from one of a variety of PCB Manufacturers. Typically, the minimum quantity for a custom PCB is five. Shipping options vary significantly in cost and shipping time. Plan on at least a week from the time of order to the PCBs arrival.

### Ordering the Controller PCB

1. Select a PCB Fabrication Company
a. JLPCB (https://jlcpcb.com/)
b. PCBWay (https://www.pcbway.com/)
c. OSH Park (https://oshpark.com/)
d. Seeed Fusion PCB (https://www.seeedstudio.com/fusion_pcb.html)
2. Create an account or use a guest login.
3. Upload the Gerber Files.
4. Select the fabrication options:
a. PCB Layers: 2 Layers
b. PCB Quantity: 5
c. PCB Thickness: 1.5 mm
d. Surface Finish: HASL
e. PCB Color: Choose what you like. Note that certain colors may impact build time.
f. The default settings for the other settings should work.
5. Select shipping option.
a. Shipping options and costs vary significantly. Select the best option based on your budget and timing.
6. Submit the order.

### Customization Guide

The device can be printed in the user’s desired colour.

## MAKER GUIDE

Files available at https://github.com/makersmakingchange/Lift-Switch | Page 6 of 22

### 3D Printing Guide

### 3D Printing Summary

Metrics | Single Unit
Total Print Time (min) | 1:51
Total Number of Components | 3
Typical Total Mass (g) | 13.4
Typical Number of Print Setups | 1

### 3D Printing Settings

Print File Name | Qty | Total Print Time (hr:min) | Mass (g) | Infill (%) | Support (Y/N) | Layer Height/ Nozzle Diameter(mm) | Notes
Lift_Switch_Base | 1 | 0:41 | 5.2 | 20 | N | 0.2/0.4
Lift_Switch_Top | 1 | 1:07 | 8.0 | 20 | N | 0.2/0.4
Lift_Switch_Power_Switch | 1 | 0:03 | 0.2 | 20 | N | 0.2/0.4

### Post-Processing

- Remove any stringing or blobs

### Examples of Quality Prints

## MAKER GUIDE

Files available at https://github.com/makersmakingchange/Lift-Switch | Page 7 of 22

### Assembly Guide

### Required Components

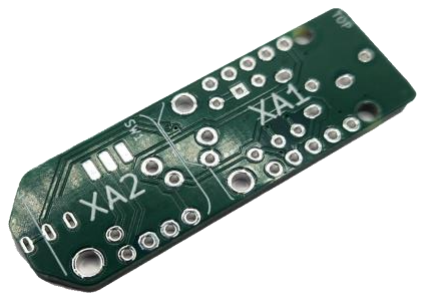
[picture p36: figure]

A

Blank Lift Switch
PCB | QTY 1 | B

Adafruit Trinket
M0 Board | QTY 1 | C

Power Supply
Board | QTY 1

D

3.5 mm jack/aux
port
QTY 1 | E | Solid-state relay | QTY 1 | F | 330 Ω resistor | QTY 1
G | Push button | QTY 1 | H | Power switch | QTY 1 | I

3.5 mm digital
output plug QTY 1

## MAKER GUIDE

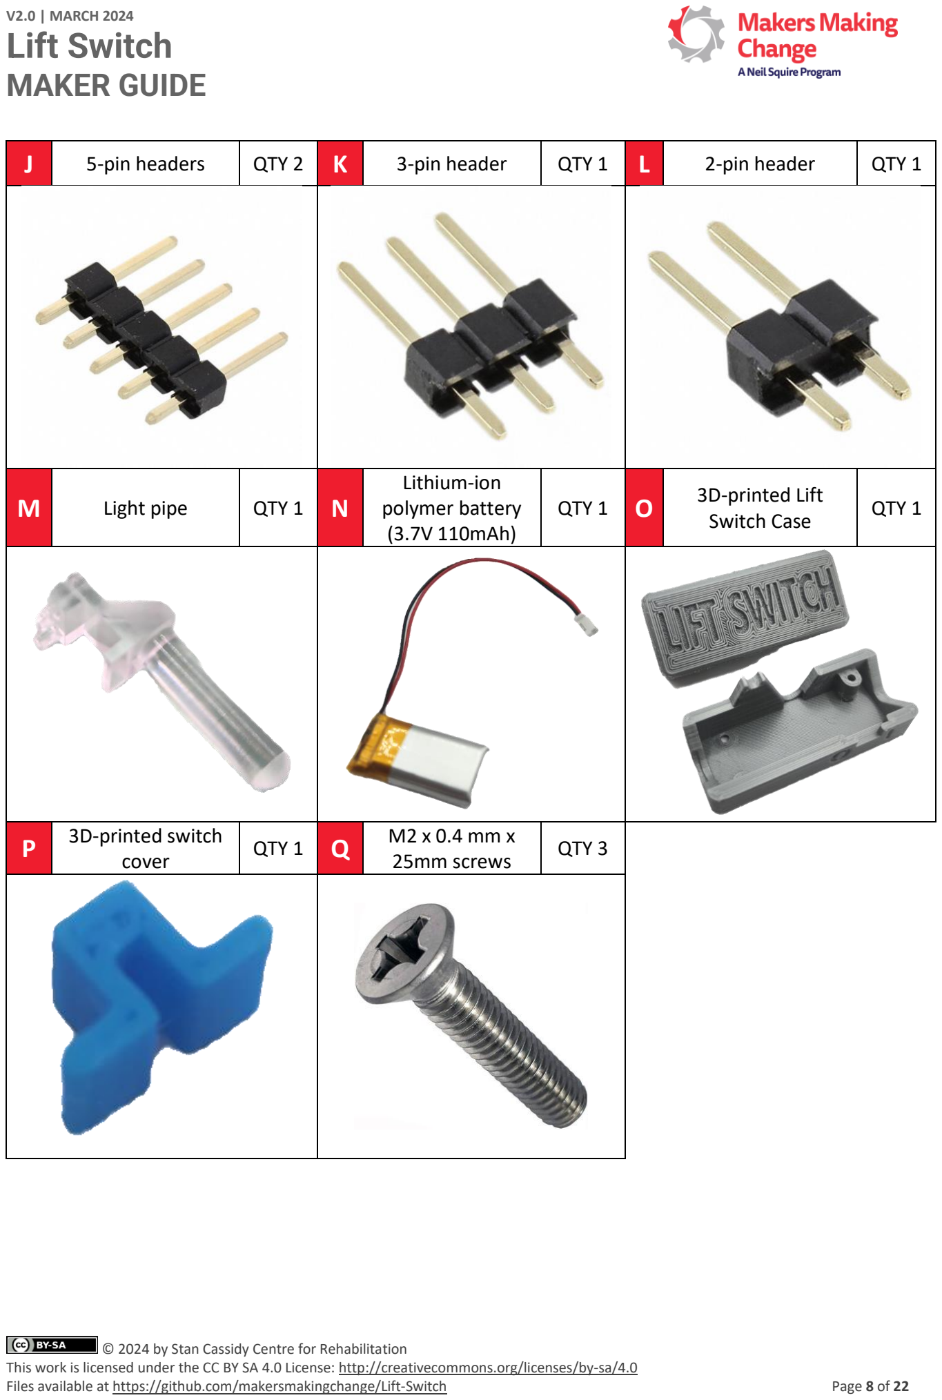
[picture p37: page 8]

Files available at https://github.com/makersmakingchange/Lift-Switch | Page 8 of 22
J | 5-pin headers | QTY 2 | K | 3-pin header | QTY 1 | L | 2-pin header | QTY 1
M | Light pipe | QTY 1 | N

Lithium-ion
polymer battery
(3.7V 110mAh)

QTY 1 O

3D-printed Lift
Switch Case

QTY 1

P

3D-printed switch
cover

QTY 1 Q

M2 x 0.4 mm x
25mm screws QTY 3

## MAKER GUIDE

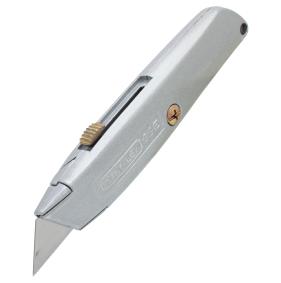
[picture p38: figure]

Files available at https://github.com/makersmakingchange/Lift-Switch | Page 9 of 22

### Required Tools

Fine-tipped soldering iron | Solder | Flush Cutters
Utility knife | Breadboard or small clamp | Electrical tape
Multimeter | Micro-USB cable | Assistive Switch and Switch Tester (for testing)

You will also need a personal computer with Arduino IDE software installed. See instructions for flashing the device.

### Required Personal Protective Equipment (PPE)

- Protective eyewear

## MAKER GUIDE

Files available at https://github.com/makersmakingchange/Lift-Switch | Page 10 of 22

### Assembly Instructions

Step 1: Insert and solder the 3.5 mm Jack

Begin with the blank PCB (A) and 3.5 mm jack (D).

Insert the 3.5 mm jack into the position labelled J1 and line up the jack with the outline on the bottom of the blank PCB as shown.

Flip the board over and solder one pin of the 3.5 mm jack in place, ensuring it stays flat and straight.

Check that the jack is straight and flat/flush to the board, if not reheat the solder joint and reposition.

Once properly positioned, solder the remaining 2 pins.

Step 2: Insert and solder the Solid-State Relay

Insert the solid-state relay (E) into the positioned labelled U1 and line up with the outline on the PCB next to the 3.5 mm jack as shown.

Note that orientation of the relay matters. Ensure it matches the image shown, with the dot on the relay oriented towards the ‘notch’ outlined on the board, and furthest from the jack.

Flip the board over and solder the relay in place, ensuring it stays flat and straight.

## MAKER GUIDE

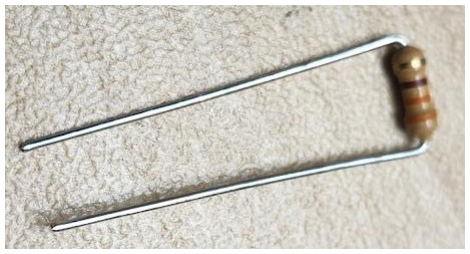
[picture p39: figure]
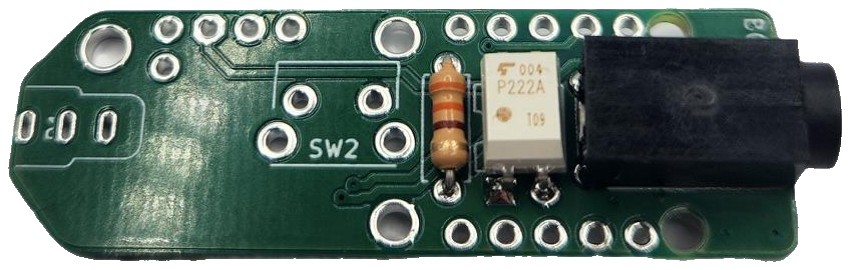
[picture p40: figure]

Files available at https://github.com/makersmakingchange/Lift-Switch | Page 11 of 22
Step 3: Insert and solder the Resistor

Bend the leads of the resistor (F) into a U-shape.

Insert the resistor into position R1, through the holes adjacent to the relay as shown. Orientation of the resistor does not matter.

Flip the board over and solder the leads of the resistor in place, then trim the leads of the resistor flush with the PCB.

Your board should now look like this:

## MAKER GUIDE

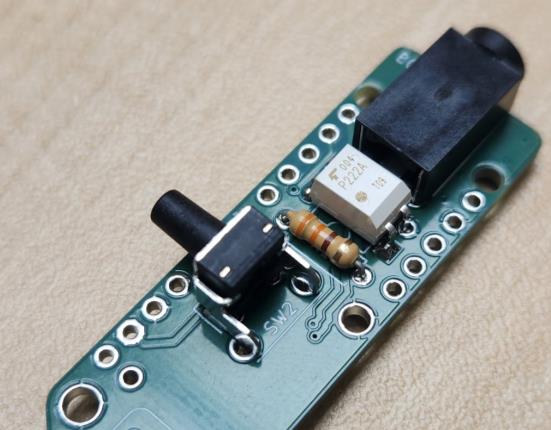
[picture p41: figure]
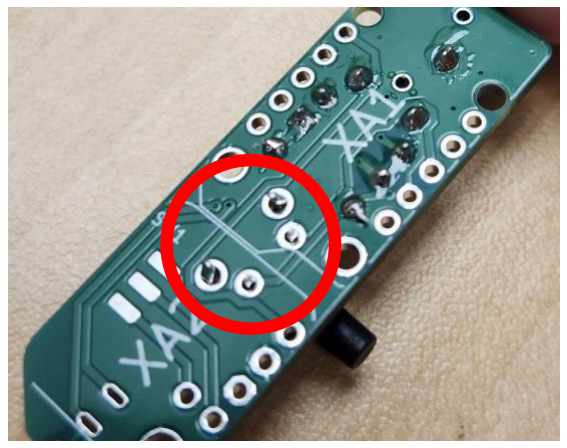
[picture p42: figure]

Files available at https://github.com/makersmakingchange/Lift-Switch | Page 12 of 22
Step 4: Insert and Solder the Push Button

Insert the push button (G) into position SW2 on the PCB as shown. It will only fit one way and will ‘snap’ into place.

Flip the board over and solder the push button in place.

## MAKER GUIDE

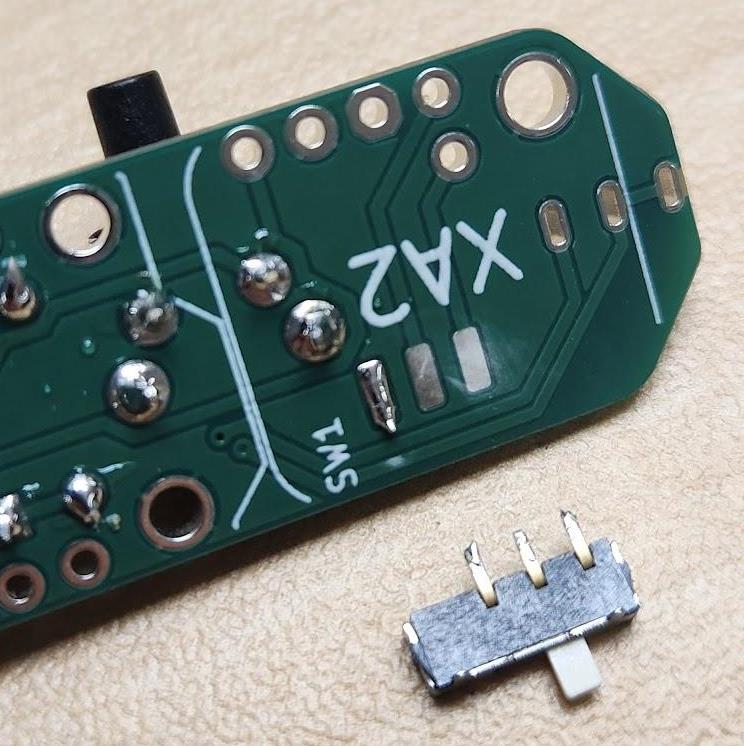
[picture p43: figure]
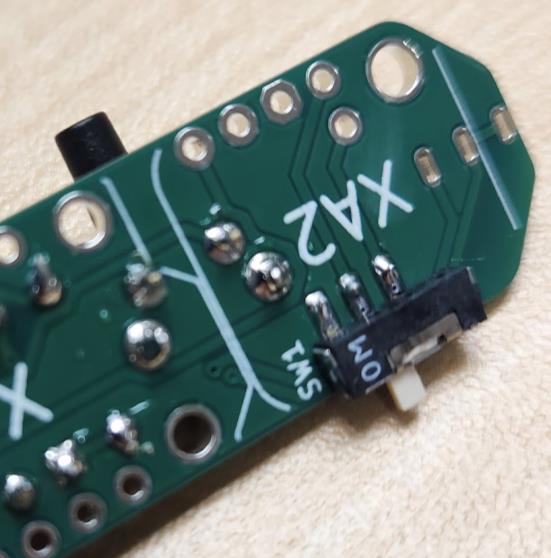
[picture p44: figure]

Files available at https://github.com/makersmakingchange/Lift-Switch | Page 13 of 22
Step 5: Position and Solder the Power Switch

Flip the PCB to the other side.

The power switch (H) is soldered to the other side of the board, that doesn’t yet have any components soldered to it. At position SW1, apply a small dab of solder onto 1 of the 3 pads of the PCB as shown. Tin the bottoms of the leads of the power switch.

Flip the power switch over and pinch the PCB and the power switch together. The “feet” of the switch will be flush with the edge of the PCB. Solder the first lead to the PCB. Ensure the switch is still flush with the PCB before soldering the other two leads.

Ensure soldering on each pad doesn’t bridge. Test the power switch with a multimeter to ensure it has been soldered properly. The power switch cannot be accessed after Step 8.

## MAKER GUIDE

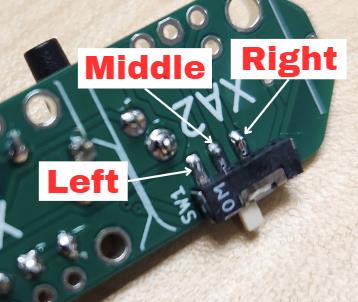
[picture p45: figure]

Files available at https://github.com/makersmakingchange/Lift-Switch | Page 14 of 22
Step 5.1: Testing the Power Switch

It is recommended you test the power switch following Step 5. This can be done using a multimeter. Put the multimeter in continuity mode and orient the PCB with the 3.5 mm jack to the left, and the power switch facing you.

With the power switch to the left, touch the probes of the multimeter to the left and right pads of the power switch. If soldered correctly, the multimeter will beep.

With the power switch to the right, touch the probes of the multimeter to the middle and right pads of the power switch. If soldered correctly, the multimeter will beep.

## MAKER GUIDE

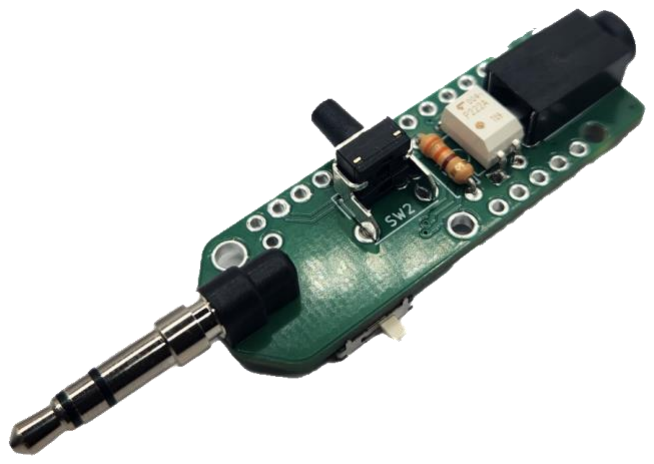
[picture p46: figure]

Files available at https://github.com/makersmakingchange/Lift-Switch | Page 15 of 22
Step 6: Insert and Solder the Digital Output Plug

Tape the 3.5 mm digital output plug (I) in position on top of the PCB as shown, ensuring it is straight and flat. Flip the board over and solder one of the leads into place.

Remove the tape and check the positioning of the 3.5 mm digital output plug again before soldering the other two leads.

Your board should now look like this:

## MAKER GUIDE

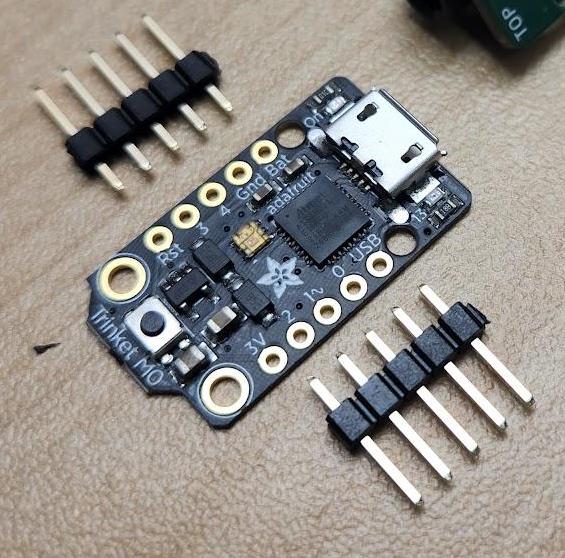
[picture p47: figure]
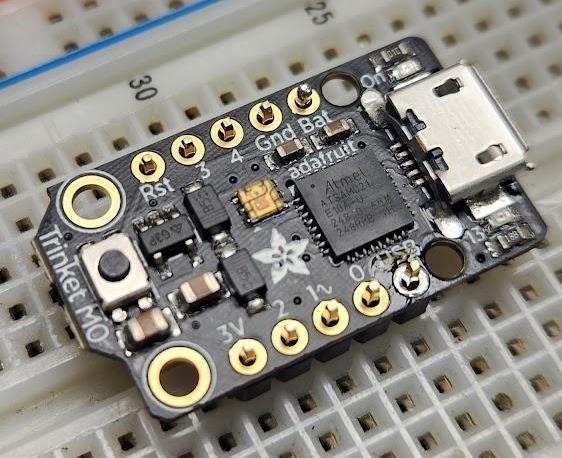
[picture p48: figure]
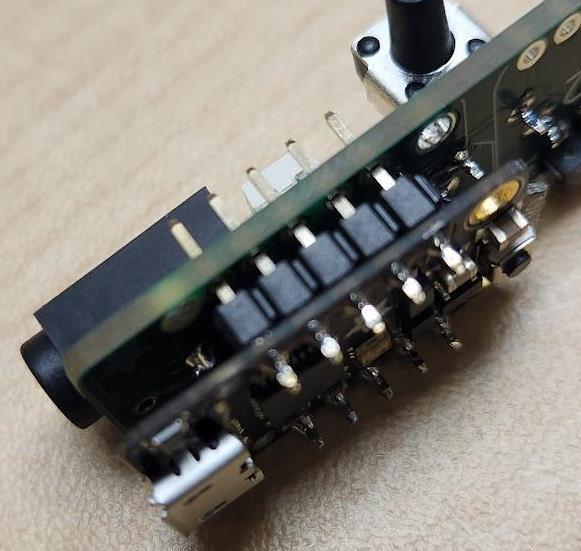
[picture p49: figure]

Files available at https://github.com/makersmakingchange/Lift-Switch | Page 16 of 22
Step 7: Insert and Solder the Trinket M0 Board

To assemble the trinket M0 board (B), place the two 5-pin headers (J) with the long side down into the breadboard.

Line up the trinket M0 board with the 5-pin headers. Ensure you do not put the pins through the larger mounting holes on either side. Solder the 5-pin headers in place.

Alternatively, if you do not have a breadboard, you may use a clamp to hold the trinket M0 board while soldering the 5-pin headers in place. You will need to be diligent to ensure the headers are not crooked.

Insert the 5-pin headers from the Trinket M0 board into the XA1 position on the PCB. Ensure the USB port is facing the nearest edge of the PCB. Note that the trinket M0 board is mounted on the opposite side of the PCB to the 3.5 mm jack. Ensure you do not put the pins through the larger mounting holes on the PCB.

Solder one pin from the assembled Trinket M0 board to the PCB, check that the headers are flush with the PCB, and then solder the remaining pins. If the headers are not flush with the PCB reheat the solder joint to adjust the alignment before soldering remaining pins.

## MAKER GUIDE

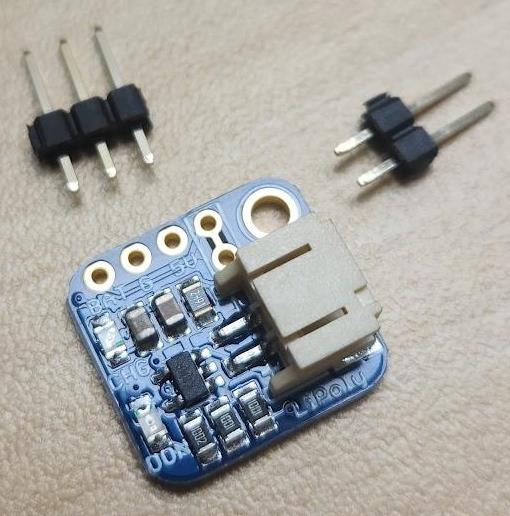
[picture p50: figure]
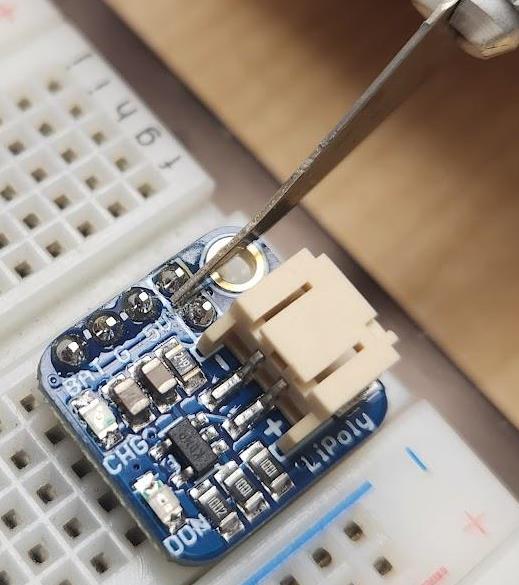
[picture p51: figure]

Files available at https://github.com/makersmakingchange/Lift-Switch | Page 17 of 22
Step 8: Insert and Solder the Power Supply Board

Using the same process described in Step 7, assemble the power supply board (C). The power supply board should be mounted on the 3- and 2-pin headers (K & L) as shown. Make sure the headers are soldered on straight and flush to the board.

Step 9: Score Between Pins on Power Supply Board

Once the headers have been soldered, use a utility knife to score a line between the pins of the 2-pin header. This is a necessary step that prevents the board from being in an “always on” state. To check that this step was successful, remove the board from the breadboard, and using a multimeter in continuity mode, touch a lead to each pin and check that it does not beep.

## MAKER GUIDE

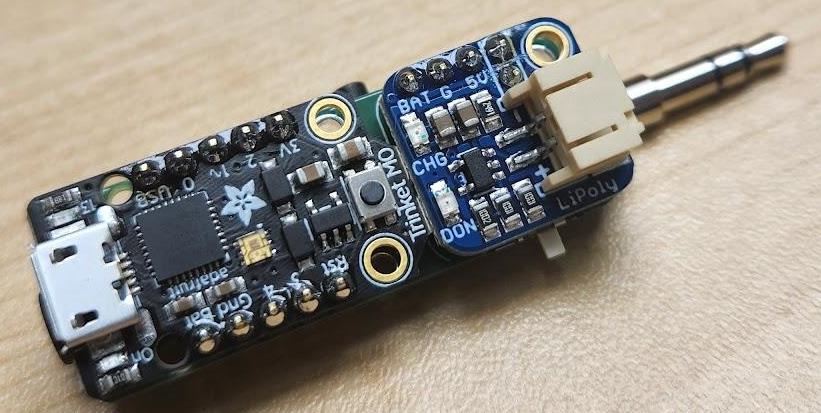
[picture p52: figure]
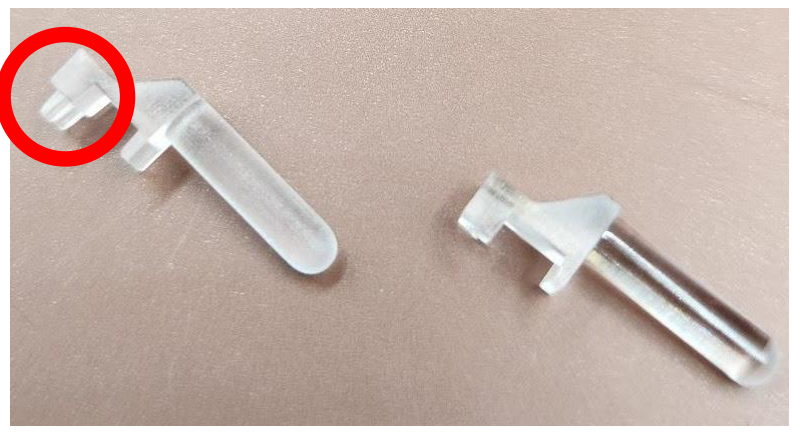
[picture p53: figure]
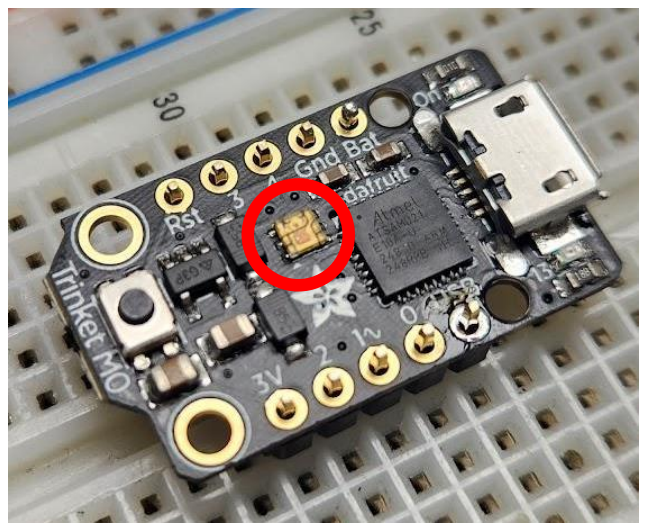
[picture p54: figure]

Files available at https://github.com/makersmakingchange/Lift-Switch | Page 18 of 22
Step 10: Solder Power Supply Board to PCB

Insert the assembled board into the XA2 position on the PCB, lining up the 2- and 3-pin headers with the PCB. Note that the power supply board is mounted on the side of the board opposite to the 3.5 mm jack. Solder the assembled power board to the PCB, ensuring it is straight and flush to the PCB.

Your board should now look like this:

Step 11: Position and Glue the Light Pipe

Before attaching the light pipe (M), trim the ‘feet’ so that the base of the pipe will sit flush against the LED.

Locate the LED on the trinket M0 board. The light pipe will sit overtop the LED, projecting to the same side of the PCB as the push button.

## MAKER GUIDE


Files available at https://github.com/makersmakingchange/Lift-Switch | Page 19 of 22

Apply a drop of hot glue to the base of the light pipe and press the light pipe into place, holding for a few seconds to allow the glue to set.

Step 12: Final Assembly

Plug the battery (N) into the power supply board. If you do not possess a multimeter, test the power switch by turning the switch on and off, ensuring the device powers down. If the power switch is not working correctly, you will have to disassemble the board and return to Step 5.

Start with the lid of the 3D-printed case (O) (the side of the case that has the text “Lift Switch”) upside-down. Place the battery in the lid, aligning the wires battery with the corner that does not have a screw hole. The battery should fit snugly in the case.

Fold the wires over, on top of the battery, and tape them in place with electrical tape. This ensures they do not get “pinched” by the circuit board.

## MAKER GUIDE


Files available at https://github.com/makersmakingchange/Lift-Switch | Page 20 of 22

Place the assembled PCB into the case overtop the wires. Ensure the 3.5 mm digital output plug and 3.5 mm jack align with their respective openings in the 3D-printed case.

Slide the 3d-printed switch cover (P) into place overtop the power switch. You should not have to force the switch cover into place; doing so may break the power switch.

Place the base of the 3D-printed case into position and screw together using the 3 screws (Q). Do not overtighten the screws.

Your Lift Switch is now assembled!

You can now proceed to the Flashing Instructions.

## MAKER GUIDE

Files available at https://github.com/makersmakingchange/Lift-Switch | Page 21 of 22

### Firmware Flashing Instructions

Step 1: Setup Arduino IDE
1. Download Arduino IDE for your operating system at https://www.arduino.cc/en/software
2. Install the Arduino IDE.
Step 2: Setup Arduino IDE for Adafruit Trinket M0 Board
1. Open Arduino IDE.
2. Click on File -> Preferences.
3. Locate the text field that says Additional Boards Manager URLs beside it.
4. Copy and paste the following link into the field as a new line: https://adafruit.github.io/arduino-board-index/package_adafruit_index.json
5. Click on OK.
6. Restart the Arduino IDE.
7. Open the Boards Manager option from the Tools-> Board-> Boards Manager...,
8. Search for “Adafruit SAMD” and select “Adafruit SAMD Boards” by Adafruit.
9. Click Install to install the board.
Step 3: Install Libraries
1. Go to Tools -> Manage Libraries…, search for “Flash Storage” and install the library “FlashStorage” by Various or Arduino.
2. Go to Tools -> Manage Libraries…, search for “Adafruit DotStar” and install the library “Adafruit DotStar” by Adafruit.
Step 4: Setup Local Code Directory
1. Download the Firmware_Files from the GitHub Repository: https://github.com/makersmakingchange/Lift-Switch/raw/main/Build_Files/Firmware_Files/LiftSwitchFirmware.zip (https://github.com/makersmakingchange/Lift-Switch/raw/main/Build_Files/Firmware_Files/LiftSwitchFirmware.zip)
2. Extract / unzip the folder to a known location.
Step 5: Upload the Code to the microcontroller.
1. Open LiftSwitchFirmware.ino with Arduino IDE.
2. Select Adafruit Trinket M0 (SAMD21) from Tools -> Board -> Adafruit SAMD Boards
3. Click on Tools -> USB Stack and select TinyUSB
4. Connect the Forest Hub using the USB cable to the computer.
5. Select the correct port from Tools -> Port menu.
6. Verify and upload the code.

## MAKER GUIDE

Files available at https://github.com/makersmakingchange/Lift-Switch | Page 22 of 22

### Testing

Turn the power switch into the on position. The LED will blink purple, then will change colour to indicate the current mode. Note that the Lift Switch ‘remembers’ the last mode it was in.

Change the modes by pressing the mode button, located on the opposite side of the power switch. The Lift Switch will cycle through the modes.

Test each mode of the Lift switch using a Switch Tester (or other switch-adapted item you possess) and an accessible switch. Please refer to the user guide for descriptions of the modes.

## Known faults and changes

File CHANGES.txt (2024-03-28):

Version 2 | 2024-Mar-28

Version 1 | YYYY-mmm-DD
 - Initial Prototype

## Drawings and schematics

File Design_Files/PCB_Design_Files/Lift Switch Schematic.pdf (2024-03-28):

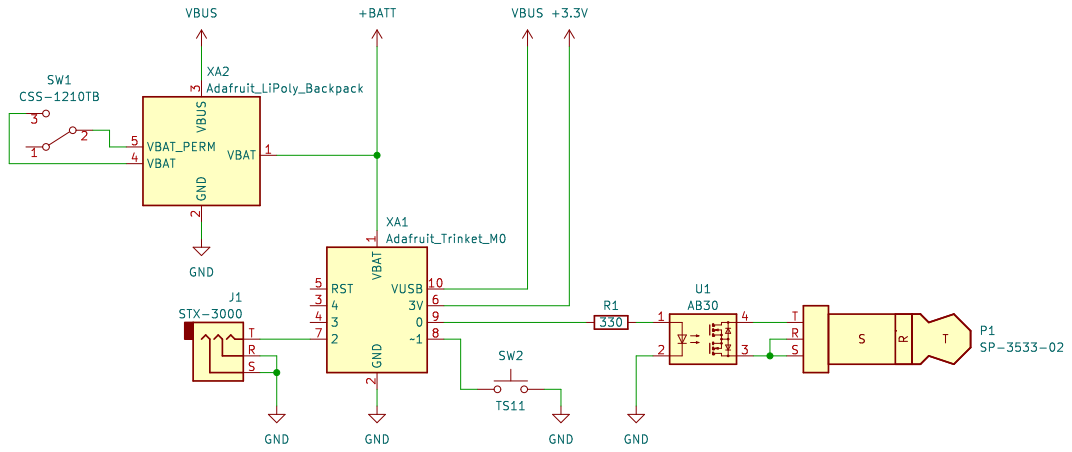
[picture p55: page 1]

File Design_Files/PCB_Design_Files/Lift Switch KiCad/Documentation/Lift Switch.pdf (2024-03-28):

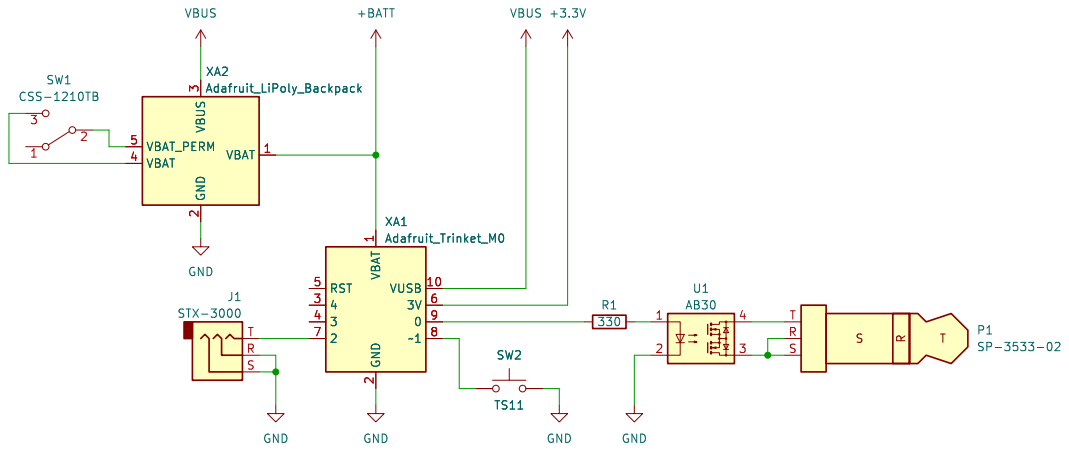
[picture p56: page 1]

Id: 1/1 Title: Lift Switch

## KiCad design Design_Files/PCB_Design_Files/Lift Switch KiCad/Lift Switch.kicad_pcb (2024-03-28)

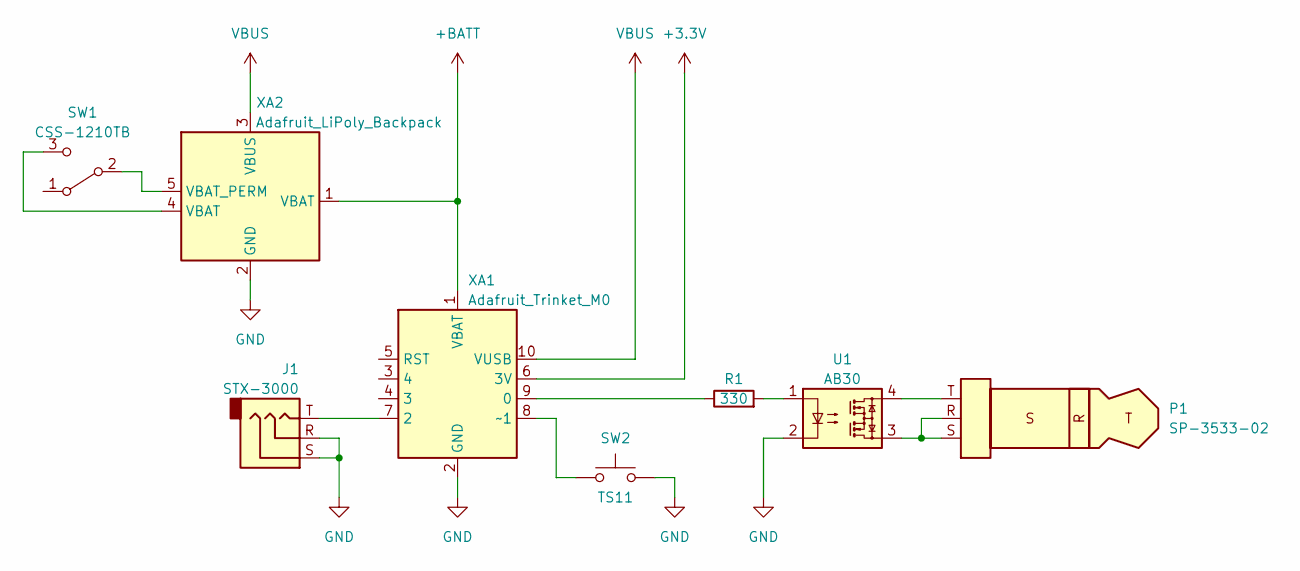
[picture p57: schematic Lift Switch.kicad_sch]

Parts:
J1: STX-3000
P1: SP-3533-02
R1: 330; R_Axial_DIN0207_L6.3mm_D2.5mm_P7.62mm_Horizontal
SW1: CSS-1210TB
SW2: TS11; TS11-674-XX-BK-XXX-RA-D
U1: AB30; DIP-4_W7.62mm
XA1: Adafruit_Trinket_M0; Adafruit Trinket M0
XA2: Adafruit_LiPoly_Backpack; Adafruit LiPoly Backpack

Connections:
+3.3V: XA1.6 (3V)
+BATT: XA1.1 (VBAT), XA2.1 (VBAT)
GND: J1.R, J1.S, SW2.2, U1.2, XA1.2 (GND), XA1.11 (MNT), XA1.12 (MNT), XA2.2 (GND), XA2.6 (MNT)
unnamed: J1.T, XA1.7 (2)
unnamed: P1.R, P1.S, U1.3
unnamed: P1.T, U1.4
unnamed: R1.1, XA1.9 (0)
unnamed: R1.2, U1.1
unnamed: SW1.2 (B), XA2.5 (VBAT_PERM)
unnamed: SW1.3 (C), XA2.4 (VBAT)
unnamed: SW2.1, XA1.8 (~1)
VBUS: XA1.10 (VUSB), XA2.3 (VBUS)

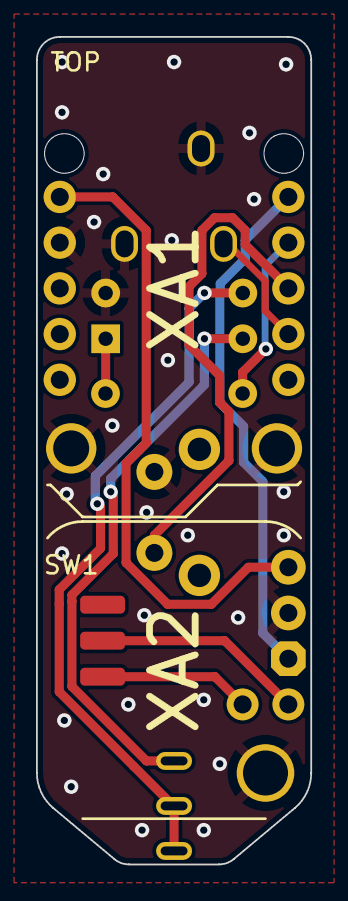
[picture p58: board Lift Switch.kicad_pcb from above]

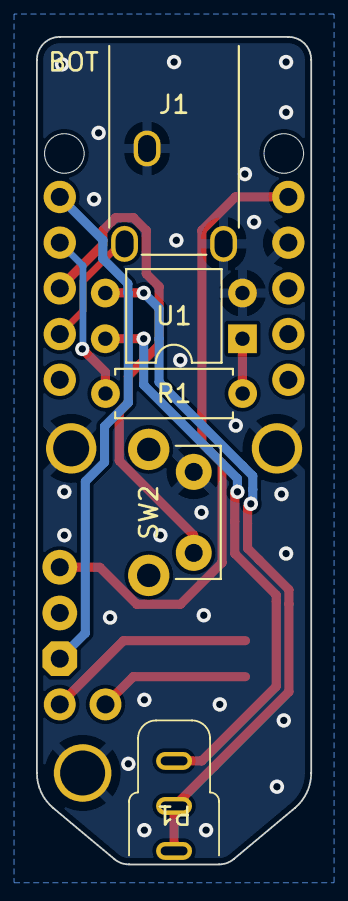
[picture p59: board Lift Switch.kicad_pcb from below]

Board: 2 copper layers, 15.2 x 46.0 mm, 8 parts (5 on the bottom side), 11 nets.

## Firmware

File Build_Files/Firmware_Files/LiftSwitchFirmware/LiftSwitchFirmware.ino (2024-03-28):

/*
                   LIFT SWITCH Mk-IV

            Stan Cassidy Center for Rehabilitation
                      Jan, 2024

            Arduino Platform: Adafruit Trinket M0

            Prcessor: ATSAMD21

            Firmware version number#: 20240105-01 v1.2

            (C)2023 STAN CASSIDY CENTER FOR REHABILITATION (SCCR)

                           ===== DISCLAMER =====
  THIS SOFTWARE IS PROVIDED "AS IS", WITHOUT WARRANTY OF ANY KIND, EXPRESS OR
  IMPLIED, INCLUDING BUT NOT LIMITED TO THE WARRANTIES OF MERCHANTABILITY,
  FITNESS FOR A PARTICULAR PURPOSE AND NONINFRINGEMENT. IN NO EVENT SHALL THE
  AUTHORS OR COPYRIGHT HOLDERS BE LIABLE FOR ANY CLAIM, DAMAGES OR OTHER
  LIABILITY, WHETHER IN AN ACTION OF CONTRACT, TORT OR OTHERWISE, ARISING FROM,
  OUT OF, OR IN CONNECTION WITH THE SOFTWARE OR THE USE OR OTHER DEALINGS IN THE
  SOFTWARE.

  ----------------------------------------------------------------------------------------------
  Special features:
     # Adafruit Trinket M0 microcontroller
     # USB B micro port for subsequent programing and interface to PC (mouse/kb emulator)
     # Accessible switch "connected" detection
     # Tri-colour status LED

  Single button operation:
     # Turn power on
     # Press MODE to change mode of operation:
         - Normal (momentary) lift switch operation  (indicated by GREEN LED)
         - Latching: lift once for on, lift a second time for off (indicatted by BLUE LED)
         - Reverse (momentary) operation (indicated by RED LED)

  LED messages:
     # MODE function - 
        GREEN to indicate normal (momentary) operation; a second press will turn the LED
        BLUE to indicate latched function; a third press will turn LED 
        RED to indicate reverse operation.
        OFF - LED goes out after 2 seconds to conserve battery power.

  FROM DOCS:
  The selected mode is indicated by the light colour:
  Blue is Latching
  Red is Reverse Acting
  Green is Momentary
.
  Mode of operation:
     # In momentary mode, the solid state relay conducts for 500 milliseconds when the input button is released (opened).
        When used as a mouse device, it provides a single left click.
     # In latch mode, the relay is latched in conducting mode when the input switch contacts are
       released (opened) then closed, the relay opens (not conducting) on second opening and closing of
       input switch contacts.
       When used as a mouse device, provides a left button press.
     # in reverse mode, contacts are open (not conducting) when switch is pressed, and conducting when switch is released.
        When used as a mouse device, provides a reversed left button press.

  Notes:
  - Ensure you have https://adafruit.github.io/arduino-board-index/package_adafruit_index.json on your Additional Boards Manager URL
      and install "Adafruit SAMD Boards" v1.7.13+
  - Choose Board "Adafruit SAMD Board -> Adafruit SAMD Trinket M0 (SAMD21)"
  - Choose USB Stack: "TinyUSB"
  - Need to install Adafruit DotStar 1.2.5+, FlashStorage 1.0.0+

  Development Notes:
  - If you get programming errors after the WIRE library inclusion - try UNPLUGGING any switches that's plugged in the 3.5mm sterio jack. Also, reset the board using the onboard reset button
*/

// External libraries:
#include <Adafruit_TinyUSB.h>
#include <Adafruit_DotStar.h>
#include <FlashAsEEPROM.h>
#include <FlashStorage.h>

#define VERSION_LIFTSWITCH "1.2"

#define MOMEN 250  // Momentary relay closure time in milliseconds

// I/O Mapping:
#define SWITCH_IN 2  // Normally open momentary adaptive switch input on pin D7 (active low)
#define SSR 0        // Solid state relay control output on pin D9 (active high)
#define MODE_SW 1    // Mode pushbutton input on pin D8 (active low)
#define VBAT_PIN  A1 // VBAT Pin in the trinket 
 
#define MOUSE_DELAY 100   // Minimum amount of time between input signals for mouse functions
#define BAUD_RATE 115200  // USB communications baud rate

#define adc_disable() (ADC->CTRLA.bit.ENABLE = 0x00) // disable ADC (before power-off)

#define MODE_MOMENT 0
#define MODE_LATCH 1
#define MODE_TIMED_LATCH 2
#define MODE_REV 3
byte opMode = MODE_MOMENT;       // Mode of operation: 0 = momentary (GREEN); 1 = latching (BLUE); 2 = timed latch (YELLOW); 3 = reverse (RED)
//Mode persistance
FlashStorage(mode_storage, byte);


byte inputButton;      // stores status of input button read
byte lastButton = 1;   // stores state of last button read
byte lastMode = 1;     // Stores state of last mode switch read
bool relayOff = true;  // status of output relay (active high)

uint32_t lastDebounceTime = 0;  // the last time the output pin was toggled
#define debounceDelay 50        // the debounce time; increase if the output flickers


//Set up the on board RGB LED
Adafruit_DotStar pixel(1, INTERNAL_DS_DATA, INTERNAL_DS_CLK, DOTSTAR_BGR);

//Config Mouse for TinyUSB
// HID report descriptor using TinyUSB's template - Single Report (no ID) descriptor
uint8_t const desc_hid_report[] = {
  TUD_HID_REPORT_DESC_MOUSE()
};
// USB HID object. For ESP32 these values cannot be changed after this declaration
// desc report, desc len, protocol, interval, use out endpoint
Adafruit_USBD_HID usb_hid(desc_hid_report, sizeof(desc_hid_report), HID_ITF_PROTOCOL_MOUSE, 2, false);


//Timed Latch Delay persistance
int32_t timedLatchDelay = 7000;  //Amount of time to hold down then timed latch. Will be read out of flash memory. This is default
FlashStorage(timedLatchDelay_storage, unsigned long);

void setup() {

  //Might want to turn off the ADC
  // Read through the init in wiring.c to see what we might be able to turn off to save power
  //set_sleep_mode(SLEEP_MODE_STANDBY); // will use this more later
  adc_disable();

  //Set up 'Friendly' names when plugged into a computer (Instead of just 'Trinket M0' showing up)
  TinyUSBDevice.setManufacturerDescriptor("SCCR");
  TinyUSBDevice.setProductDescriptor("Lift Switch");

  //https://github.com/adafruit/ArduinoCore-samd/issues/128 - not sure we have a onboard buck regulator in the SAMD21 we can use https://cdn-learn.adafruit.com/downloads/pdf/adafruit-trinket-m0-circuitpython-arduino.pdf
  //SUPC->VREG.bit.SEL = 1;

  // I/O configuration:
  pinMode(SWITCH_IN, INPUT_PULLUP);
  pinMode(MODE_SW, INPUT_PULLUP);
  pinMode(SSR, OUTPUT);

 // pinMode(VBAT_PIN, INPUT);

  pixel.begin();

  usb_hid.begin();

  Serial.begin(BAUD_RATE);

  //Wait for USB to time out if not connected
  unsigned long _start = millis();
  boolean _serialConnected = true;
  while(!Serial)         //Wait until the serial port is opened with a 5 second timeout
  {
    //Blink while looking for serial
    pixel.setPixelColor(0, 50, 0, 50);  //Turn on VIOLET LED 
 
    //Make the LED breath
    for (int i = 0; i < 255; i+=2) {
      pixel.setBrightness( i );
      pixel.show(); //Show the color
      delay(3);
    }
    for (int i = 255; i > 0; i-=2) {
      pixel.setBrightness( i );
      pixel.show(); //Show the color
      delay(3);
    }

    if (millis() - _start > 5000)
    {
      //NO Serial connected
      _serialConnected = false;
      break;
    }
  }

  // Print info so that when a switch is plugged in, we can see the firmware version / date it was last programmed
  Serial.println(F("START " __FILE__ " from " __DATE__ "\r\nUsing firmware version " VERSION_LIFTSWITCH));

  // wait until device mounted. Might need to change in the future if we're also using bluetooth (not just Serial USB)
  if (_serialConnected)
  {
    while (!TinyUSBDevice.mounted()) delay(1);
  }

  opMode = readMode();
  timedLatchDelay = readTimeLatchedDelay();

  //Indicate the initial mode by turning on the LED
  pixel.setBrightness( 255 );
  pixel.setPixelColor(0, getModeColor(opMode));  //Turn on GREEN LED - the color for the start-up mode. 
  pixel.show(); //Show the color
  delay(2000); // Delay 2 seconds so user can see the mode they're in. 
  pixel.setPixelColor(0, 0);  //Turn LED OFF 
  pixel.show(); //Show the color

}  // end of setup()


void loop() {
  // poll gpio once each 10 ms
  delay(10);

  // Check if Mode change is requested
  bool _changedMode = doMode();

  if (_changedMode) 
  {
    pixel.setPixelColor(0, getModeColor(opMode));  //Turn off the LED
    pixel.show(); //Show the new mode

    delay(2000); // Delay 2 seconds so user can see the mode they're in. 

    // TURN OFF LED
    pixel.setPixelColor(0, 0);  //Turn off the LED
    pixel.show(); //Show the new mode

    storeMode(opMode);
  }
/*
  //Check to see if enough time has passed to read the button. Once the button is pressed, we'll STOP reading it for a bit to wait for it to settle down
  if ((millis() - lastDebounceTime) > debounceDelay) {
    // Check status of input button and perform function
    uint8_t reading = digitalRead(SWITCH_IN);  // Read current state of the button. We'll use this to debounce. reading will = 0 (LOW) when the button is pressed
    if (reading != inputButton) {  // Something has changed
      {
        // reset the debouncing timer
        lastDebounceTime = millis();
        inputButton = reading;
      }
    }
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

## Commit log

2024-03-28 Initial commit files
    [5-Pin Header - Male - 2.54mm.step, Adafruit protrinket backpack.step, CSS-1210TB.STEP, CUI_DEVICES_SP-3533-02.step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]
2024-03-28 Initial documentation commit
    [Device_Name_BOM.xlsx, LiftSwitch_Base_v2.SLDPRT, Lift_Switch_BOM.csv, Lift_Switch_BOM.xlsx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]
2026-02-23 Updated enclosure files
